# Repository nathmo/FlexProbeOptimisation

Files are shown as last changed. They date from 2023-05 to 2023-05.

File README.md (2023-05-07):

# FlexProbeOptimisation
this repo contain code to compute and properties
of an adjustable stiffness force sensor and optimise
it's parameter to get the best resolution possible

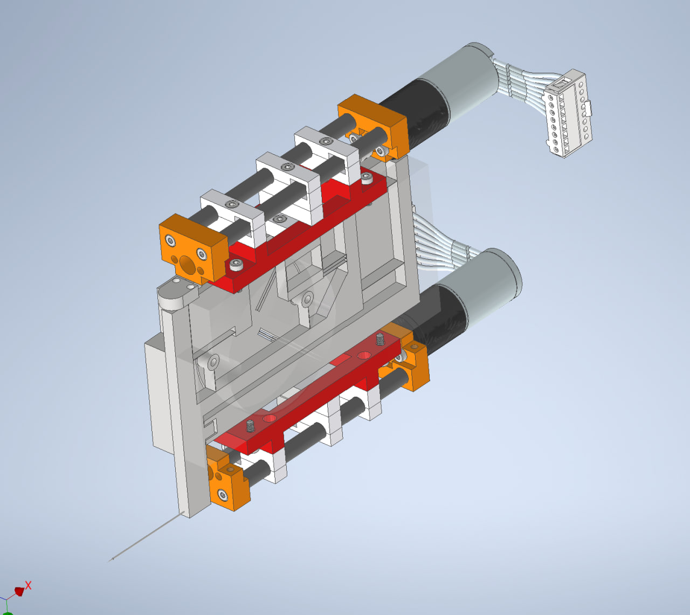
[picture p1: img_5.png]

you will find the parameter in the excel Sheet Settings.xlsx
to import it easily into Autodesk inventor and thus having a parametric desing

after running the code, report.md is updated with the result

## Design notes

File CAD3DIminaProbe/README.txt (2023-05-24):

this folder contain each itteration of our CAD.
Linear axis is the assembly of our LinearAxis alone
RoueMDF is the file for the MDF tunned flex mechanism
V4Roue is the folder with the real CAD of the mechanism

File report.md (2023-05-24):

# Paramètre utiliser pour le calcul des résultat

# 2 Principe de fonctionnement

## 2.6)
Mise en évidence des concepts originaux et explications spécifiques à la solution retenue

# 3) Dimmensionnement

## 3.0 Intro
Target :
Plage de mesure : Fmax > 50 mN

Résolution de mesure : RF < 500 nN. Il s’agit du principal critère d’optimisation du capteur
qui consiste à minimiser la valeur RF(keq,min)

Correction du zéro : le système de réglage doit permettre de corriger des forces parasites
selon l’axe X dans l’intervalle suivant : −1 mN <= Fparasite <= 1 mN

nous allons dabord dimmensionné le système de correction du zéro 
car sa rigidité doit êre prise en compte dans la rigidité total du système.

## 3.1 réglage du zéro
meme actionneur utilisé pour les deux fonction :
q_z = 0.05 mm / tour (vis différentiel : 0.5 mm et 0.45 mm )
d_z = M2.5 et M3
R_alphaz = 1.6° (backlash du reducteur) sinon 0.024245°=360/(512 code/tour * 29 (réducteur))
R_z = 0.003367 micron (q_p/(512*29 (reducteur))) ou 0.22222 micron (backlash)
plage de z max = 0-1mm

résolution point A : Rfz
Plage de réglage demandé : -1mF à 1mF
nombre de position possible du moteur = 4'500
Rfz = deltaFparasite / nombre de position possible du moteur = 2mN/4500= 4.444*10^{-7}[N]

dans le but de diminuer l'impacte de la rigidité de la table sur le reste du systeme,
nous avons utiliser la roue pour diminué la course rensentie par la table
à lame d'un facteur 8. en échange il nous à fallu fournir 8 fois plus de force
donc pas +-1mN mais +-8mN
rigidité des lames : (2 lames*ratio transformation de 8 -> 16 N/m par lame)

nous avons donc essayer de tuner les parametre de notre table pour obtenir la rigidité total de 16 N/m:
avec une table à 2 lamme  mais la longeur devenais trop grande.

Nous avons donc du faire une table avec la plus grande 
hauteur possible : 20 mm de long, 8mm de largeur et 100 um d'épaisseur
nous avons obtenu 220 N/m.

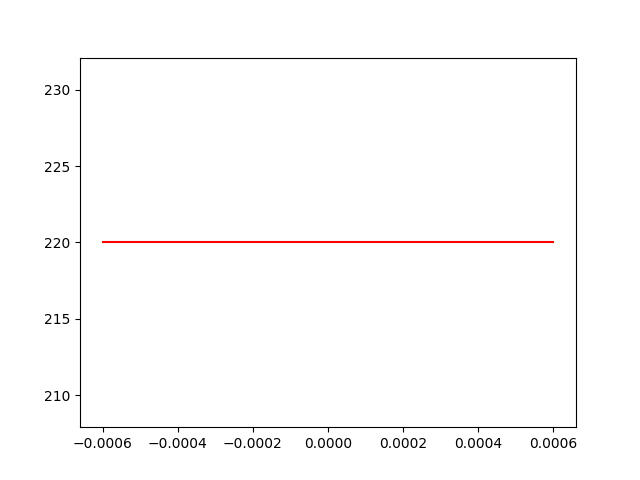
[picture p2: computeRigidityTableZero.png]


soit une plage de réglage de entre -110mN et 110mN
avec une résolution de 0.04888 mN

## 3.2 rigidité 

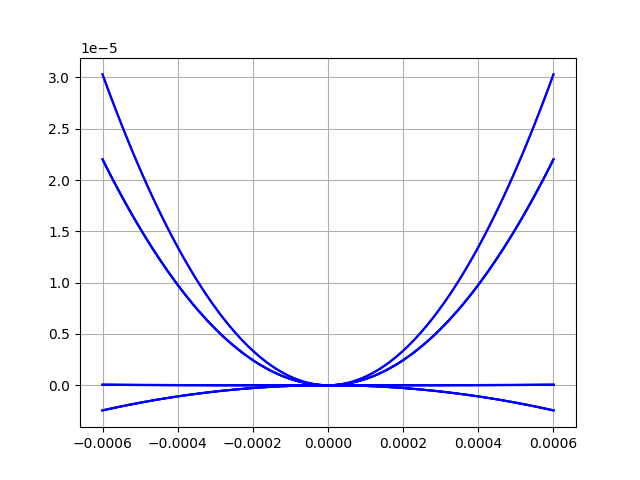
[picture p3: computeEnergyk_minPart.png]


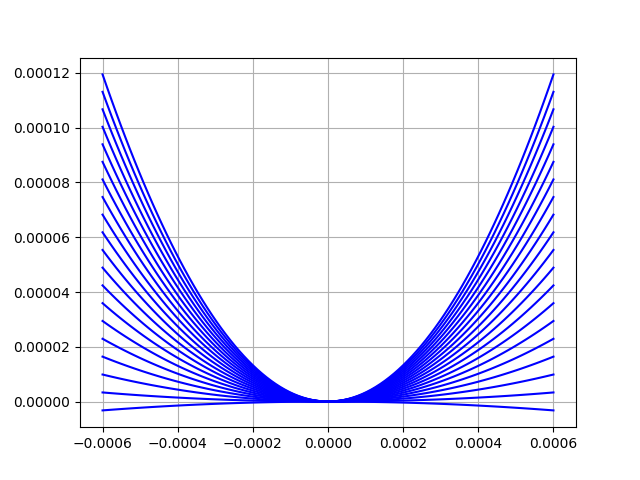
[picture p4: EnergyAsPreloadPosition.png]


meme actionneur utilisé pour les deux fonction :
q_p = 0.05 mm / tour (vis différentiel : 0.5 mm et 0.45 mm )
d_p = M2.5 et M3
R_alphap = 1.6° (backlash du reducteur) sinon 0.024245°=360/(512 code/tour * 29 (réducteur))
R_p = 0.003367 micron (q_p/(512*29 (reducteur))) ou 0.22222 micron (backlash)
plage de p max = 0-1mm

pour déterminer la force que le pusher doit appliquer on graphe le k_eq du system
jusqua trouver les bonnes forces
on aimerais que nos rigidité sois entre : 50 N/m et 

pour la borne minimal on veux une résolution 500 nN
mais la résoltion du cateur est de 10 micron
ce qui nous donne une rigidité à 0.05 N/m ou mieux (0 N/m)

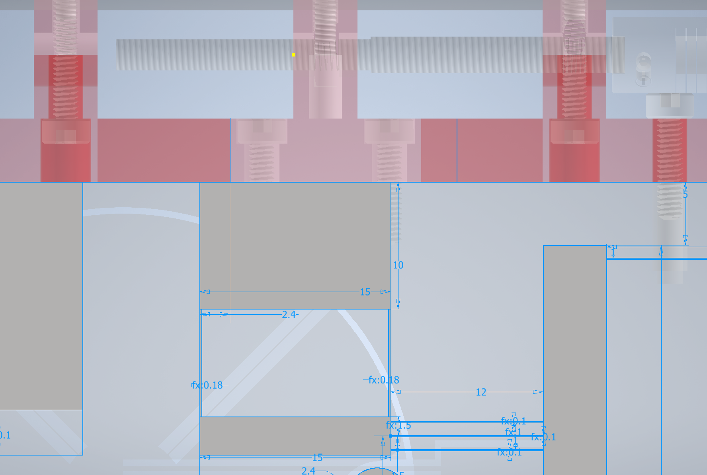
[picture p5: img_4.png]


 (rigidité (N/m) en fonction de la position)
on peut voir que les parametre qui rentre bien dans le range sont :
2.53 N au minimum
2.63 N au maximum
Ces valeurs représente la force à appliquer par lamme.
comme il y as 3 lamme  en parralel, il faut en réalité 
forceMin = 2.53*3=7.59 N
forceMax = 2.63*3=7.89 N
si on voulais maximiser la résoltion il faudrait que le
0.3 N de force revienne à une course d'un 1mm de la table à lamme.
hors cela impliquerais une déformation de 26 mm latérallement.

hors pour des raison géométrique, il est difficile d'avoir une tel course.

nous choississont donc limiter la course de notre table à 2 mm 
de plus nous allons précontraidre la table de 1mm à l'assemblage 
pour profiter de la précharge et supprimer le jeux sur l'actionneur
en plus de profiter d'une meilleure résolution de la force de précharge
dans la région d'interet.

cela impose à notre table d'avoir une rigidité de 7.89N/0.002m=3'945 N/m
et nous pourrons ainsi obtenir une résolution de rigidité.
pour se faire on utilise le nombre de position distincte que l'axe linéaire
peut prendre (4500) répartis sur la plage d'un 1mm ce qui nous donne
3.945 N / 4500 point = 0.8766 mN de résolution pour la force de précharge

de plus on vois qu'on est largement en dessous de la force maximal que 
peut tollérer l'actionneur linéaire.

on voit sur le graphique que la table a lame à bien la rigidité de 3945 N/m
attendu.

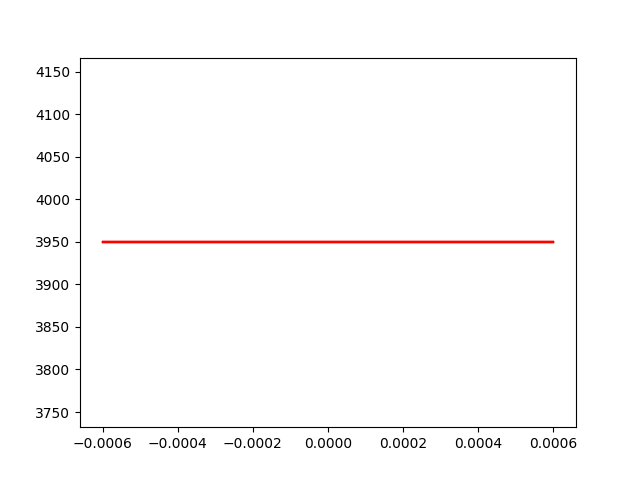
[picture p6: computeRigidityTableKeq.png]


## 3.3 débattement des articulation
(formule mouvement relatif)
0.5 mm sur toute les lames
(légerement plus sur la roue est nécéssaire mais simplifier à 1 mm)

## 3.4 contrainte max flamage + casse chaque lame
(vérifier que les lame supporte une déformation de 2-3mm (demander TRISTAN))

## 3.5 Couple moteur
Nominal torque (max. continuous torque) = 3.33 mNm
réducteur ratio = 29
Nominal Torque on shaft = 29*3.33 mNm = 96.57 mNm
(we neglect loss and add a 20% safety margin at the end)
radius = M3-> 3.2mm/2=1.6mm (on prend le plus gros diametre des 2)
force max = ominal Torque/radius = 60.35 N
donc on se limite à 50 Newton par sécurité
( et  on vois par la suite que la force de précontrainte est inférieur dans tout les cas)

## 3.6 Energie de chaque systeme + total 



Energie total pour le réglage de force sur toute la plage de x
(échelle en unité SI, Joule par metre (avec une précharge N pour chaque courbe))
attention. la force de précontrainte est calculer est calculer par lame.
pour avoir la valeurs total il faut multiplier par le nombre de lame qui transmettent la force
et la au point de rigidité minimum avec un graph pour chaque élément

Energie de chaque systeme + 



## 3.7 dérivé energie = Force en fonction de X

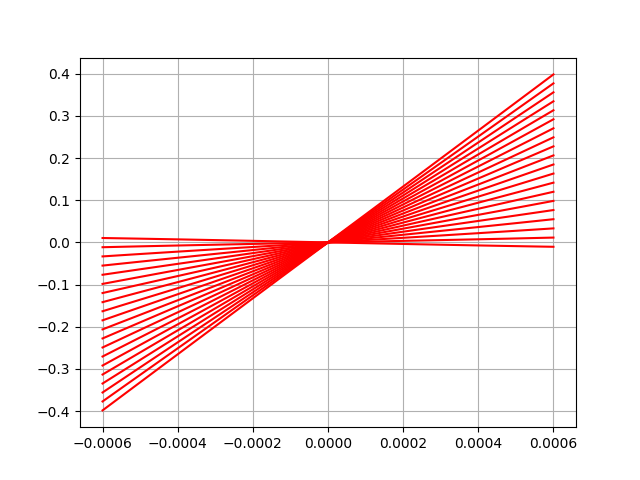
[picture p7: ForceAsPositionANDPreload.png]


(échelle en unité SI, N/m par N)
attention. la force de précontrainte est calculer est calculer par lame.
pour avoir la valeurs total il faut multiplier par le nombre de lame qui transmettent la force
## 3.8  polynome Force en fonction de x degrée 2 (a0 a1 a2)

F (x) ∼= Fpoly3(x) = a0 + a1 · x + a2 · x2 + a3 · x3 ;

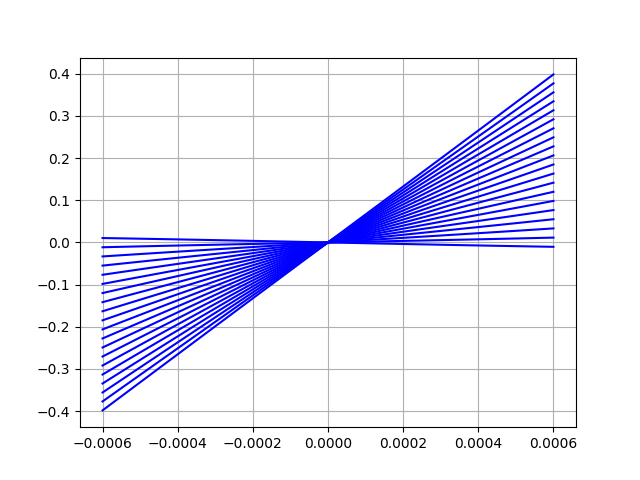
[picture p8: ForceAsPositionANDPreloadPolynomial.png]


## 3.9 k_eq min et k_eq max (dérivé encore)
Determiner la plage de réglage de rigidité de votre mécanisme keq,min 6 keq 6 keq,max correspon-
dants aux réglages pmax , respectivement pmin (note : vérifier bien que keq,min > 0) 

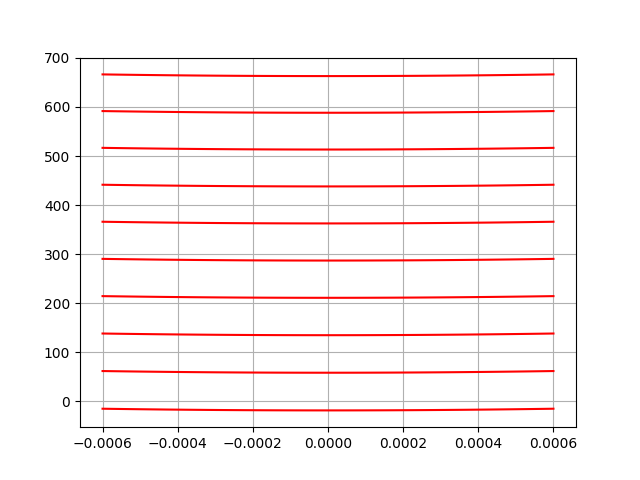
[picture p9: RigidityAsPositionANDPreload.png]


## 3.10 non-linéarité relative mu pour p min et max

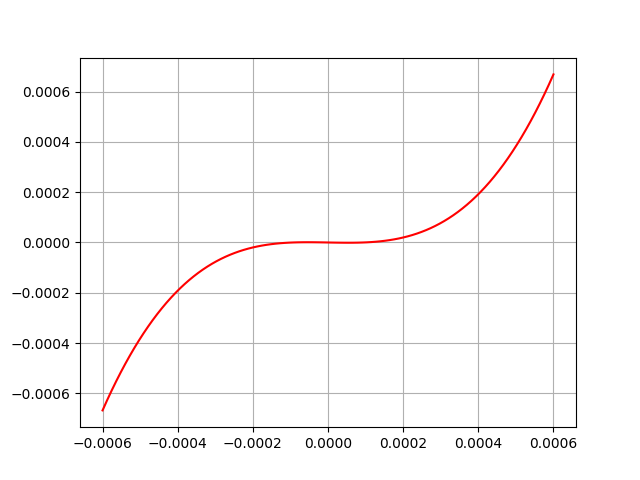
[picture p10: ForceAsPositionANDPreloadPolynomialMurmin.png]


p_min :

mu_r_pmin=-113797755.63251112401

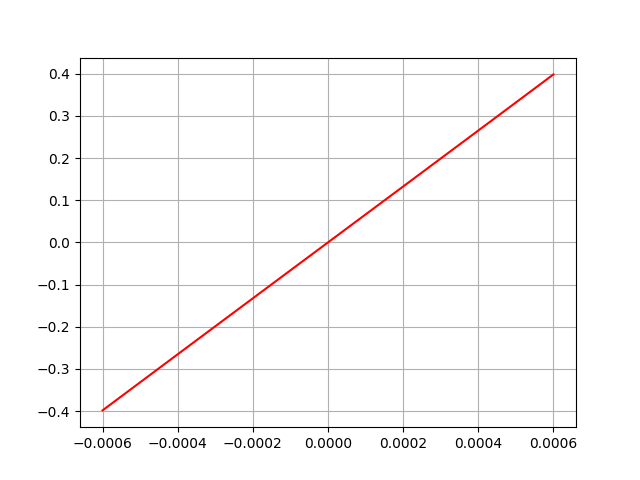
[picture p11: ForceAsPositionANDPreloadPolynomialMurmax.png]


p_max :

mu_r_pmax=4778.5669276376367747

## 3.11 graph de poly + num

Tracer sur un même graphique les fonctions F (x), Fpoly3(x) et Flin(x) 

red = numerical
blue = polynomial
green = linear

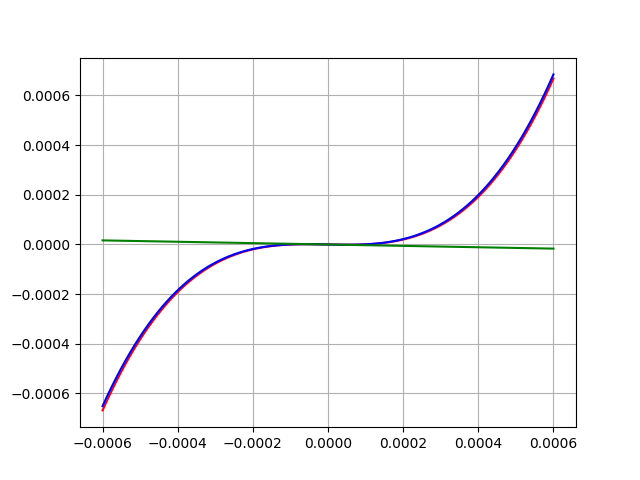
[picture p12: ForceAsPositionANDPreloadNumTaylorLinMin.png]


(nous avons ajouter un leger offset pour voir que les lignes sont bien superposé)

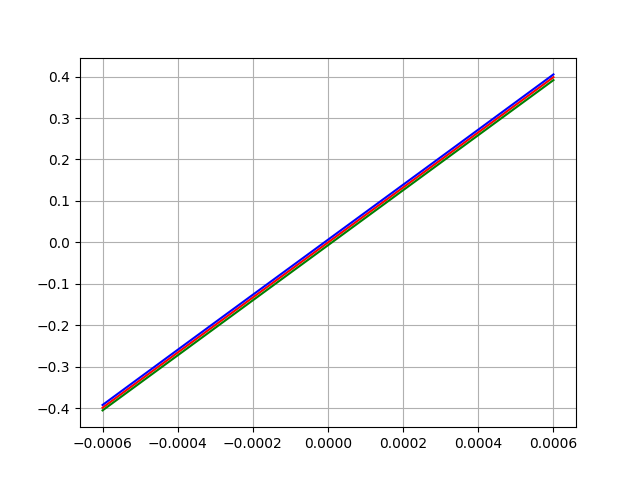
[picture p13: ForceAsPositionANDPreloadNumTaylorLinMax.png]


## 3.12 résolution

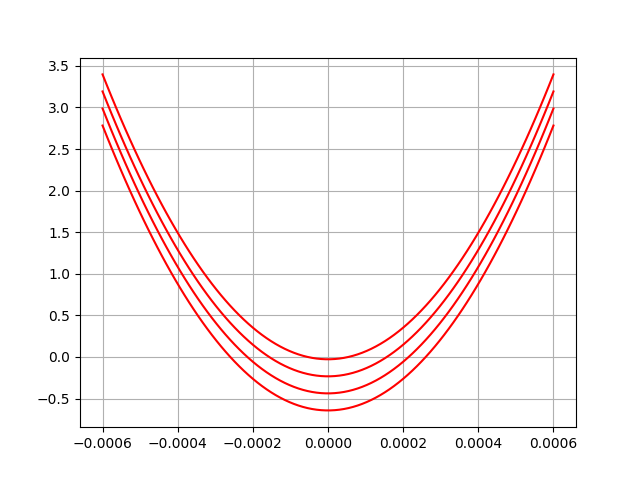
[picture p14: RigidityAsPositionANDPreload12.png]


( chaque ligne montre un réglage de résolution)
ce graphe montre la résolution a 4 point conséqutif de réglable de la précontrainte)
dans le pire des cas on as une rigidité :
RigidityPmin=0.2 N/m

RigidityFPmax=2.5N/m

RFminpmin = 2 nF
RFminpmax = 25 nF

mais dans le meilleures des cas elle peut etre encore meilleure

## 3.13 Force Max mesurable à p_min et p_max
avec Fmax ∼= keq · smax

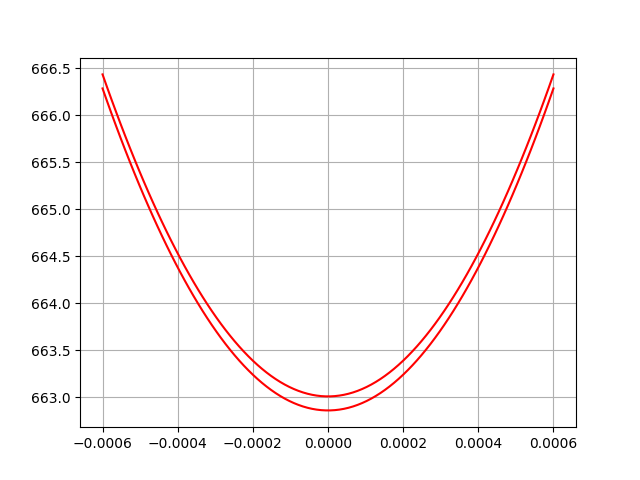
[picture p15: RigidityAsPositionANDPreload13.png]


Fmax_p_min=0.000006810 N (6.8 uN)

Fmax_p_max=0.3405 N

## 3.14 gamme dynamique virtuelle (nombre de point ) de la Force mesurable
(Force MAX / Force min)

DFv : gamme dynamique virtuelle du capteur de force : DFv = Fmax(keq,max)/RF(keq,min)

(échelle en unité SI, N/m par N)
attention. la force de précontrainte est calculer est calculer par lame.
pour avoir la valeurs total il faut multiplier par le nombre de lame qui transmettent la force

DFv=0.3405 N/2 nF=170'250'000

# 5 Construction

## 5.1) choix de construction

## 5.2) Matériaux

aliage titane-6Al-4V

tres peu magnétique
compatible avec le vide, dégaze peu
110 GPa

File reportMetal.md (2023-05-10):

# Paramètre utiliser pour le calcul des résultat

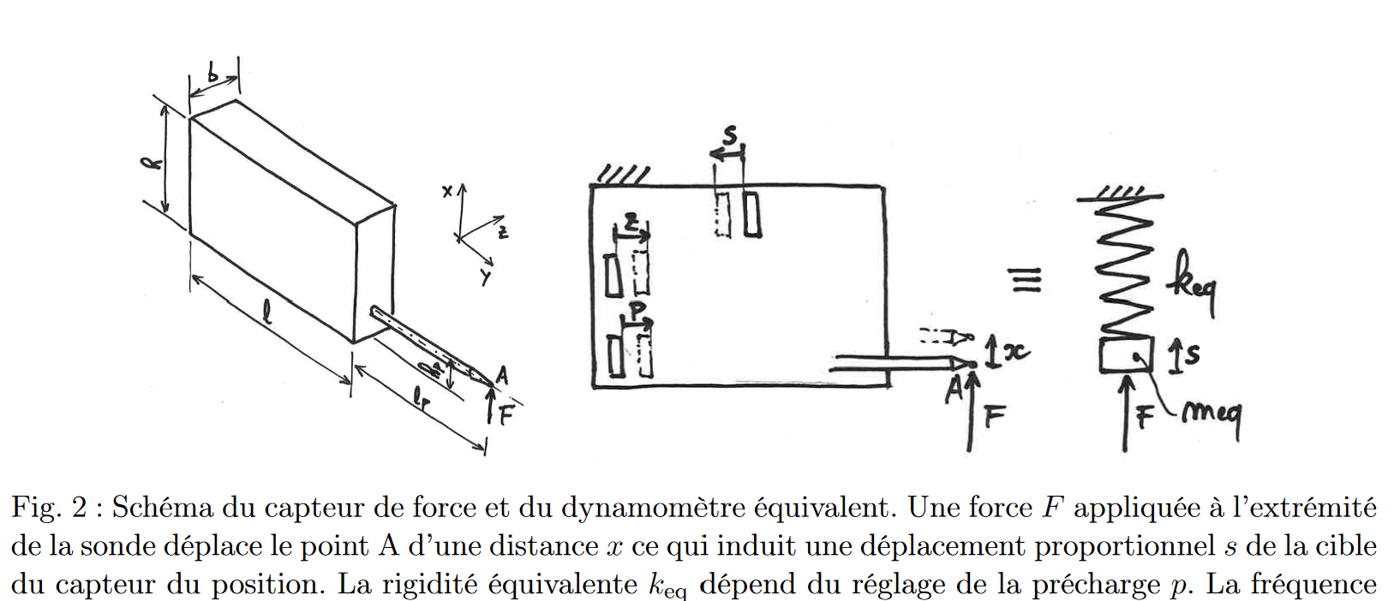
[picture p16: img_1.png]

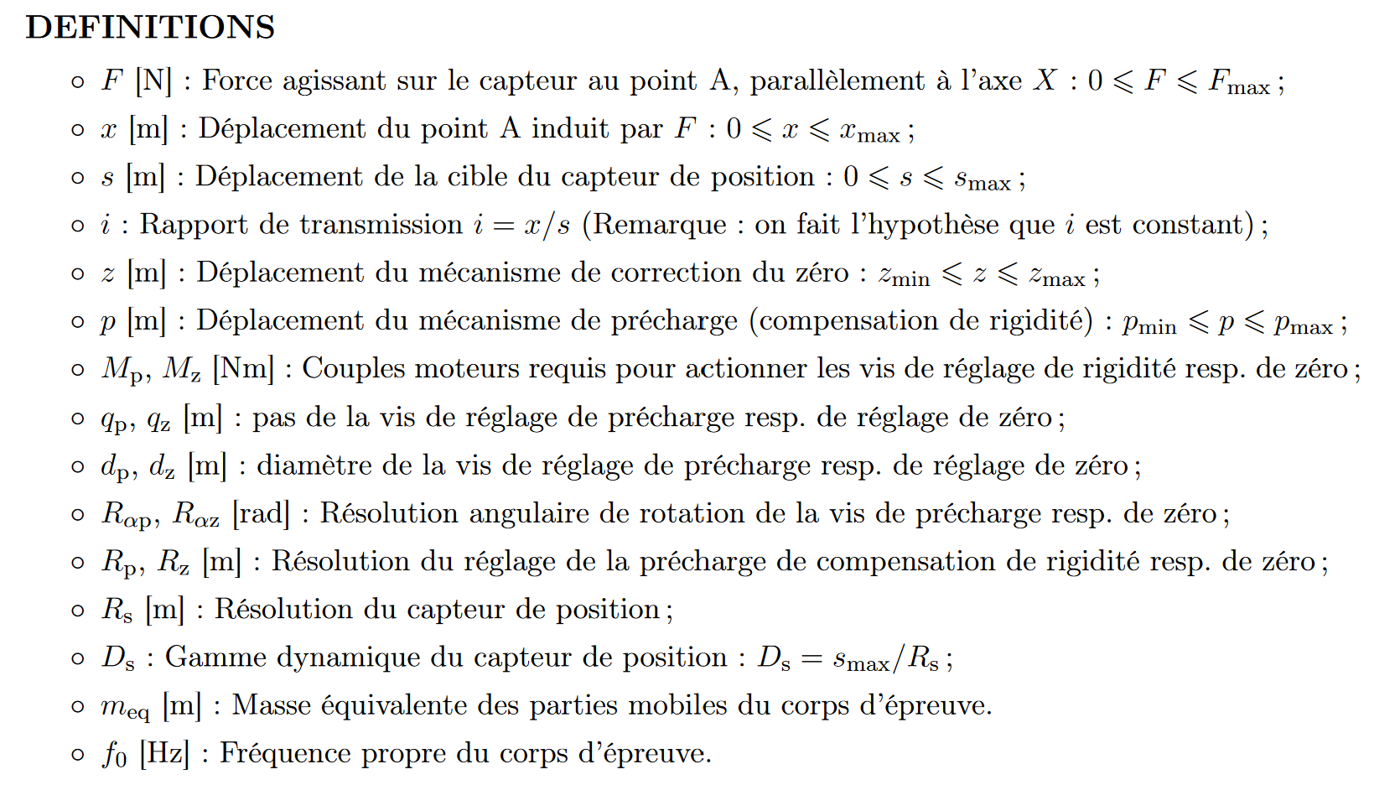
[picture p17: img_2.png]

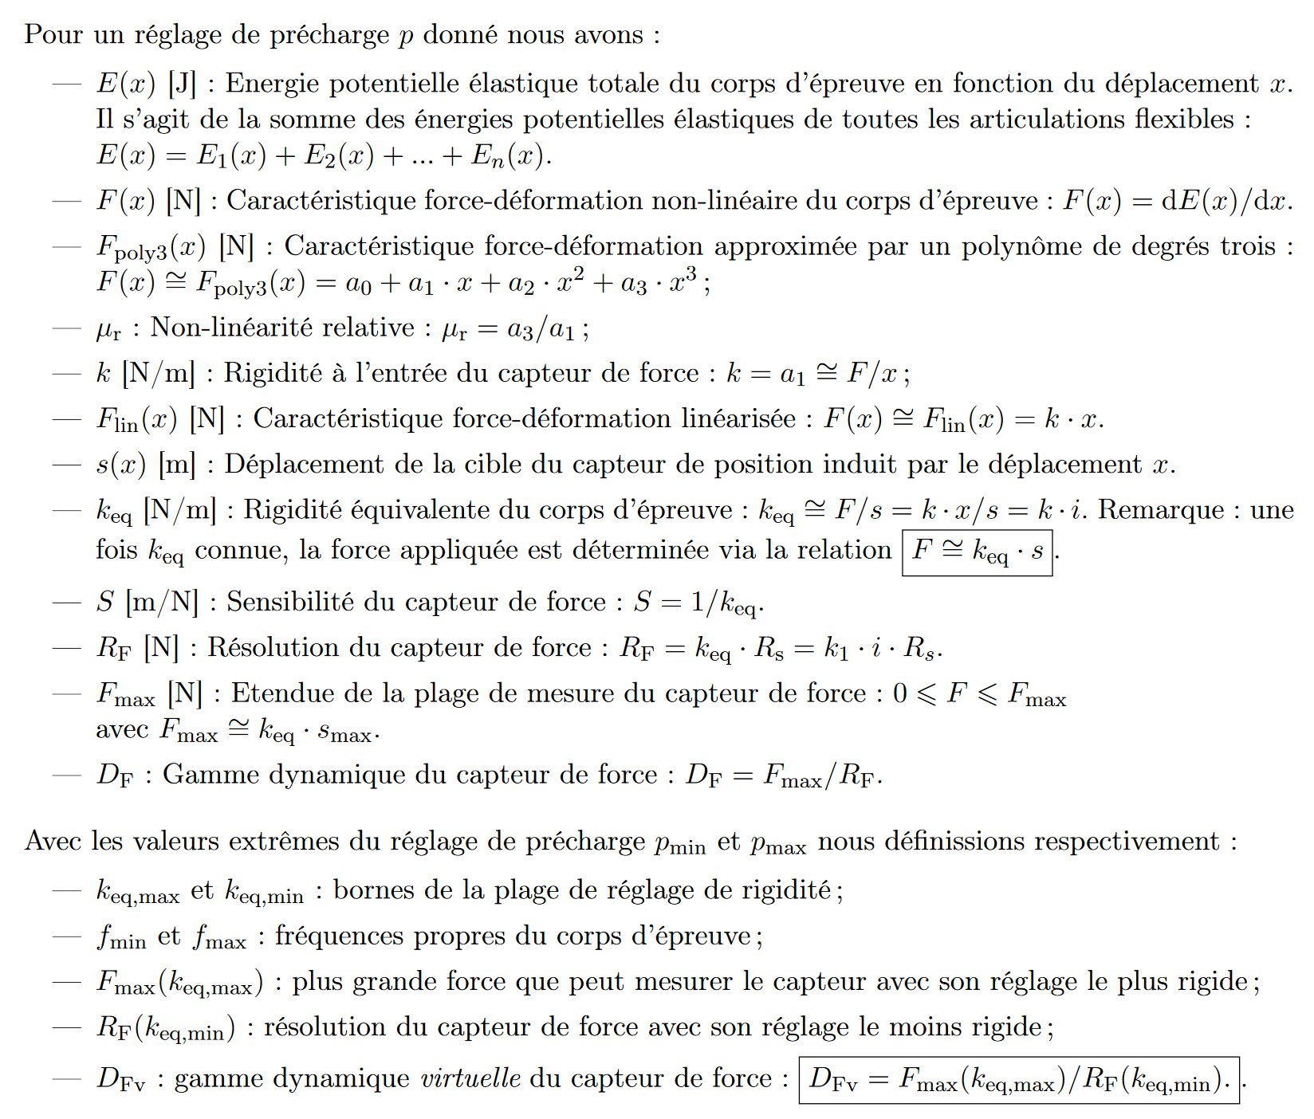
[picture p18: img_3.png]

# 2 Principe de fonctionnement

## 2.6)
Mise en évidence des concepts originaux et explications spécifiques à la solution retenue

# 3) Dimmensionnement

## 3.0 Intro
Target :
Plage de mesure : Fmax > 50 mN

Résolution de mesure : RF < 500 nN. Il s’agit du principal critère d’optimisation du capteur
qui consiste à minimiser la valeur RF(keq,min)

Correction du zéro : le système de réglage doit permettre de corriger des forces parasites
selon l’axe X dans l’intervalle suivant : −1 mN <= Fparasite <= 1 mN

nous allons dabord dimmensionné le système de correction du zéro 
car sa rigidité doit êre prise en compte dans la rigidité total du système.

## 3.1 réglage du zéro
meme actionneur utilisé pour les deux fonction :
q_z = 0.05 mm / tour (vis différentiel : 0.5 mm et 0.45 mm )
d_z = M2.5 et M3
R_alphaz = 1.6° (backlash du reducteur) sinon 0.024245°=360/(512 code/tour * 29 (réducteur))
R_z = 0.003367 micron (q_p/(512*29 (reducteur))) ou 0.22222 micron (backlash)
plage de z max = 0-1mm

résolution point A : Rfz
Plage de réglage demandé : -1mF à 1mF
nombre de position possible du moteur = 4'500
Rfz = deltaFparasite / nombre de position possible du moteur = 2mN/4500= 4.444*10^{-7}[N]

dans le but de diminuer l'impacte de la rigidité de la table sur le reste du systeme,
nous avons utiliser la roue pour diminué la course rensentie par la table
à lame d'un facteur 8. en échange il nous à fallu fournir 8 fois plus de force
donc pas +-1mN mais +-8mN
rigidité des lames : (2 lames*ratio transformation de 8 -> 16 N/m par lame)

nous avons donc essayer de tuner les parametre de notre table pour obtenir la rigidité total de 16 N/m:
avec une table à 2 lamme  mais la longeur devenais trop grande.

Nous avons donc du faire une table avec la plus grande 
hauteur possible : 20 mm de long, 8mm de largeur et 100 um d'épaisseur
nous avons obtenu 220 N/m.


soit une plage de réglage de entre -110mN et 110mN
avec une résolution de 0.04888 mN

## 3.2 rigidité 
meme actionneur utilisé pour les deux fonction :
q_p = 0.05 mm / tour (vis différentiel : 0.5 mm et 0.45 mm )
d_p = M2.5 et M3
R_alphap = 1.6° (backlash du reducteur) sinon 0.024245°=360/(512 code/tour * 29 (réducteur))
R_p = 0.003367 micron (q_p/(512*29 (reducteur))) ou 0.22222 micron (backlash)
plage de p max = 0-1mm

pour déterminer la force que le pusher doit appliquer on graphe le k_eq du system
jusqua trouver les bonnes forces
on aimerais que nos rigidité sois entre : 50 N/m et 

pour la borne minimal on veux une résolution 500 nN
mais la résoltion du cateur est de 10 micron
ce qui nous donne une rigidité à 0.05 N/m ou mieux (0 N/m)

 (rigidité (N/m) en fonction de la position)
on peut voir que les parametre qui rentre bien dans le range sont :
2.53 N au minimum
2.63 N au maximum
Ces valeurs représente la force à appliquer par lamme.
comme il y as 3 lamme  en parralel, il faut en réalité 
forceMin = 2.53*3=7.59 N
forceMax = 2.63*3=7.89 N
si on voulais maximiser la résoltion il faudrait que le
0.3 N de force revienne à une course d'un 1mm de la table à lamme.
hors cela impliquerais une déformation de 26 mm latérallement.

hors pour des raison géométrique, il est difficile d'avoir une tel course.

nous choississont donc limiter la course de notre table à 2 mm 
de plus nous allons précontraidre la table de 1mm à l'assemblage 
pour profiter de la précharge et supprimer le jeux sur l'actionneur
en plus de profiter d'une meilleure résolution de la force de précharge
dans la région d'interet.

cela impose à notre table d'avoir une rigidité de 7.89N/0.002m=3'945 N/m
et nous pourrons ainsi obtenir une résolution de rigidité.
pour se faire on utilise le nombre de position distincte que l'axe linéaire
peut prendre (4500) répartis sur la plage d'un 1mm ce qui nous donne
3.945 N / 4500 point = 0.8766 mN de résolution pour la force de précharge

de plus on vois qu'on est largement en dessous de la force maximal que 
peut tollérer l'actionneur linéaire.

on voit sur le graphique que la table a lame à bien la rigidité de 3945 N/m
attendu.

## 3.3 débattement des articulation
(formule mouvement relatif)
0.5 mm sur toute les lames
(légerement plus sur la roue est nécéssaire mais simplifier à 1 mm)

## 3.4 contrainte max flamage + casse chaque lame
(vérifier que les lame supporte une déformation de 2-3mm (demander TRISTAN))

## 3.5 Couple moteur
Nominal torque (max. continuous torque) = 3.33 mNm
réducteur ratio = 29
Nominal Torque on shaft = 29*3.33 mNm = 96.57 mNm
(we neglect loss and add a 20% safety margin at the end)
radius = M3-> 3.2mm/2=1.6mm (on prend le plus gros diametre des 2)
force max = ominal Torque/radius = 60.35 N
donc on se limite à 50 Newton par sécurité
( et  on vois par la suite que la force de précontrainte est inférieur dans tout les cas)

## 3.6 Energie de chaque systeme + total 

Energie total pour le réglage de force sur toute la plage de x
(échelle en unité SI, Joule par metre (avec une précharge N pour chaque courbe))
attention. la force de précontrainte est calculer est calculer par lame.
pour avoir la valeurs total il faut multiplier par le nombre de lame qui transmettent la force
et la au point de rigidité minimum avec un graph pour chaque élément

Energie de chaque systeme + 


## 3.7 dérivé energie = Force en fonction de X

(échelle en unité SI, N/m par N)
attention. la force de précontrainte est calculer est calculer par lame.
pour avoir la valeurs total il faut multiplier par le nombre de lame qui transmettent la force
## 3.8  polynome Force en fonction de x degrée 2 (a0 a1 a2)

F (x) ∼= Fpoly3(x) = a0 + a1 · x + a2 · x2 + a3 · x3 ;


## 3.9 k_eq min et k_eq max (dérivé encore)
Determiner la plage de réglage de rigidité de votre mécanisme keq,min 6 keq 6 keq,max correspon-
dants aux réglages pmax , respectivement pmin (note : vérifier bien que keq,min > 0) 


## 3.10 non-linéarité relative mu pour p min et max

mu_r=0

## 3.12 résolution


( chaque ligne montre un réglage de résolution)
ce graphe montre la résolution a 4 point conséqutif de réglable de la précontrainte)
dans le pire des cas on as une rigidité :
RigidityPmin=0.2 N/m

RigidityFPmax=2.5N/m

RFminpmin = 2 nF
RFminpmax = 25 nF

mais dans le meilleures des cas elle peut etre encore meilleure

## 3.13 Force Max mesurable à p_min et p_max
avec Fmax ∼= keq · smax


Fmax_p_min=0.000006810 N (6.8 uN)

Fmax_p_max=0.3405 N

## 3.14 gamme dynamique virtuelle (nombre de point ) de la Force mesurable
(Force MAX / Force min)

DFv : gamme dynamique virtuelle du capteur de force : DFv = Fmax(keq,max)/RF(keq,min)

(échelle en unité SI, N/m par N)
attention. la force de précontrainte est calculer est calculer par lame.
pour avoir la valeurs total il faut multiplier par le nombre de lame qui transmettent la force

DFv=0.3405 N/2 nF=170'250'000

# 5 Construction

## 5.1) choix de construction

## 5.2) Matériaux

aliage titane-6Al-4V

tres peu magnétique
compatible avec le vide, dégaze peu
110 GPa

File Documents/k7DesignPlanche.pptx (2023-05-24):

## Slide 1

Groupe 37, Solution 2 : La cassette

Guidages idéaux

Guidages Flexibles

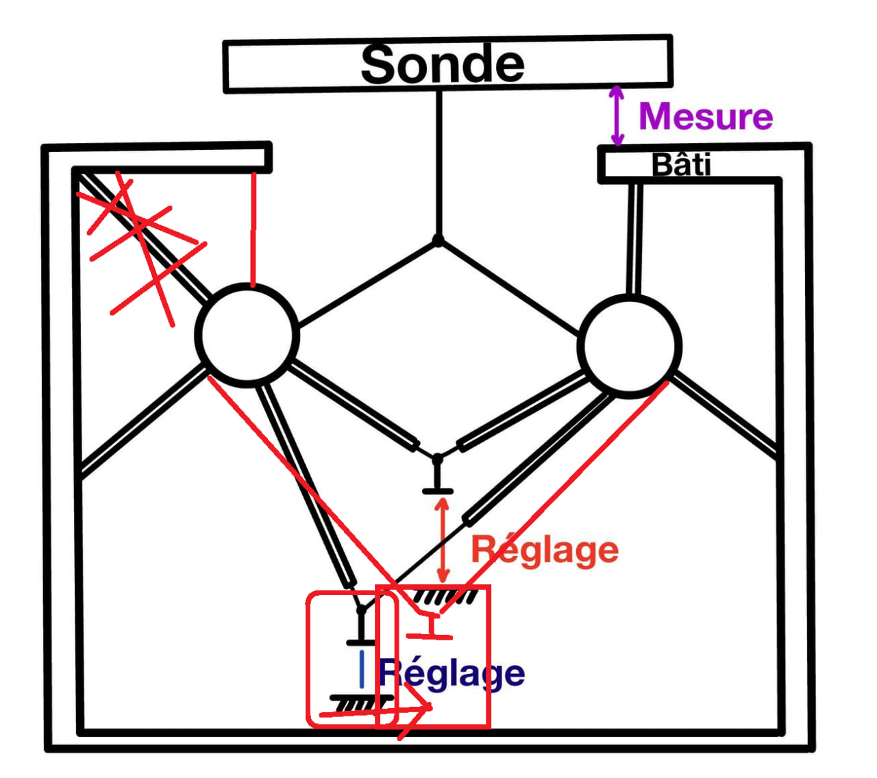
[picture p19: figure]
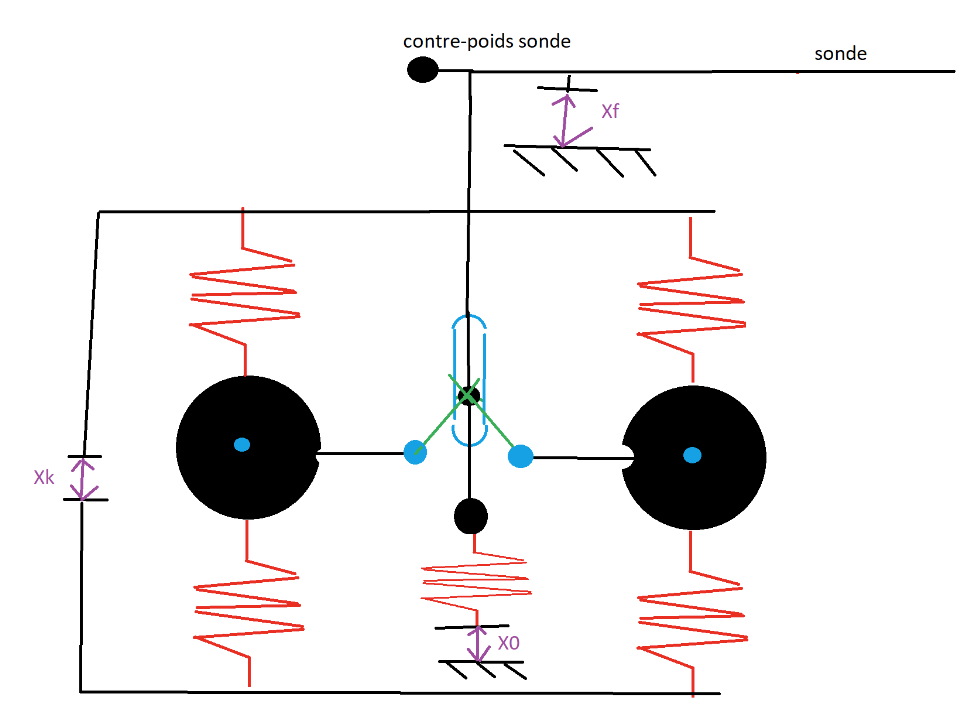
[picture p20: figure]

Mobilité de Grubler

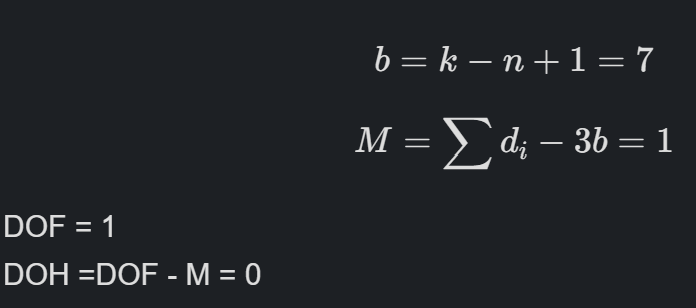
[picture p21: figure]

SFMI

de pars sont implémentions se basant sur un design de référence SFMI,
Il conserve cette propriété.

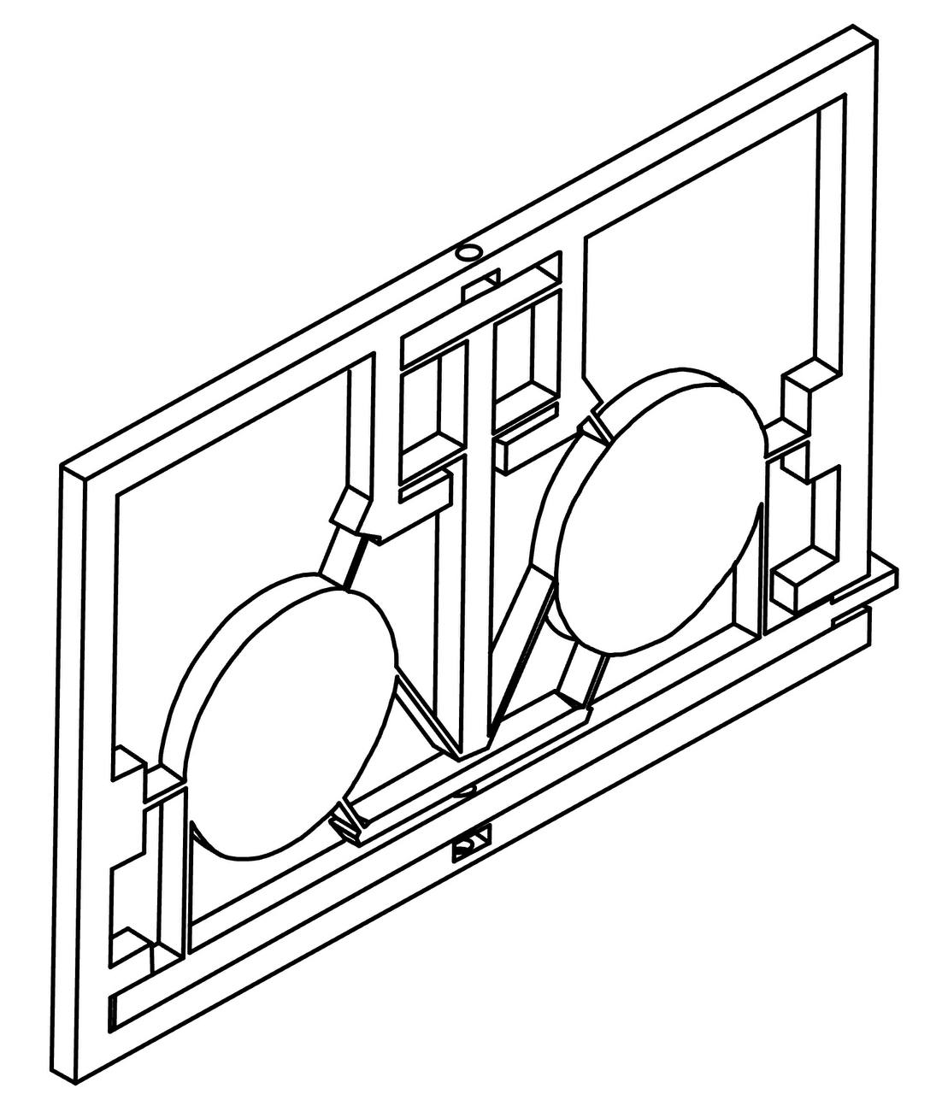
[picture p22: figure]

Ce système de Capteur de force a rigidité et position variable présente l’avantage de pouvoir être réaliser monolitiquement avec une seul pièce (et 2 boulon) mais présente une non-linéarité de la position d'équilibre en fonction de x0 ainsi qu'une non-linéarité de la rigidité en fonction de x0.
Avec un dimensionnement correct, celle-ci peuvent-être vu comme linéaire sur la course de fonctionnement.

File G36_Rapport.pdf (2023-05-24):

Conception de Mécanismes II : Projet Dynabal | Groupe 36
19 MAI 2023 | 1

### Groupe 36

Morand Nathann 296190

Ramirez Felipe 331471

Tankwa Baptiste 346039

Torres Tristan 341042

# PROJET DE CONCEPTION DE MECANIQUES II

# DYNABAL

## Table des matières

2.1.5 | Principe du système vis-écrou (anti-rotation, rattrapage des jeux, guidage vis,
2.6 | Mise en évidence des concepts originaux et explications spécifiques à la solution retenue
| 10
4.1 | Expliquer la séquence de réglage retenue pour obtenir la meilleure gamme dynamique
(rigidité, zéro, fréquence, calibration avec capteur ou tare externes etc.). ET Lister les non-
4.2 | Discuter les effets des tolérances de fabrication (typiquement ±3 µm pour l’usinage par
7.2 | Dessin de détail de la vis | Erreur ! Signet non défini.

## 1 Introduction

Le projet DYNABAL est né de la problématique d’Imina Technologies, souhaitant un capteur de force à rigidité réglable pour ses robots de haute précision, utilisés notamment dans l’industrie des semi-conducteurs.

Dans le cadre du projet DYNABAL, nous avons réalisé un mécanisme que nous avons nommé la Roue. La Roue est un capteur de force équilibré dynamiquement, avec une rigidité variable. Ce rapport détaille son principe de fonctionnement, son dimensionnement, une discussion autour de sa cohérence avec le cahier des charges et des étapes de sa construction.

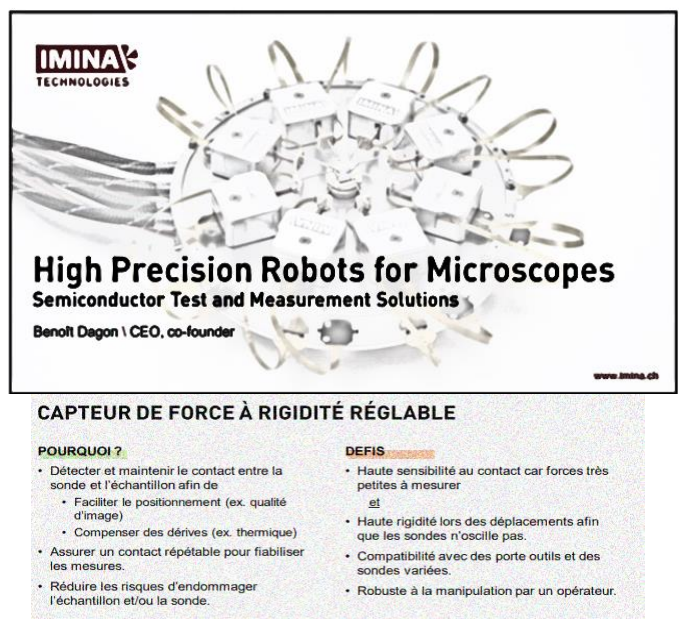
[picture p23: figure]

22 Février 2023

19 mai 2023

6 avril 2023

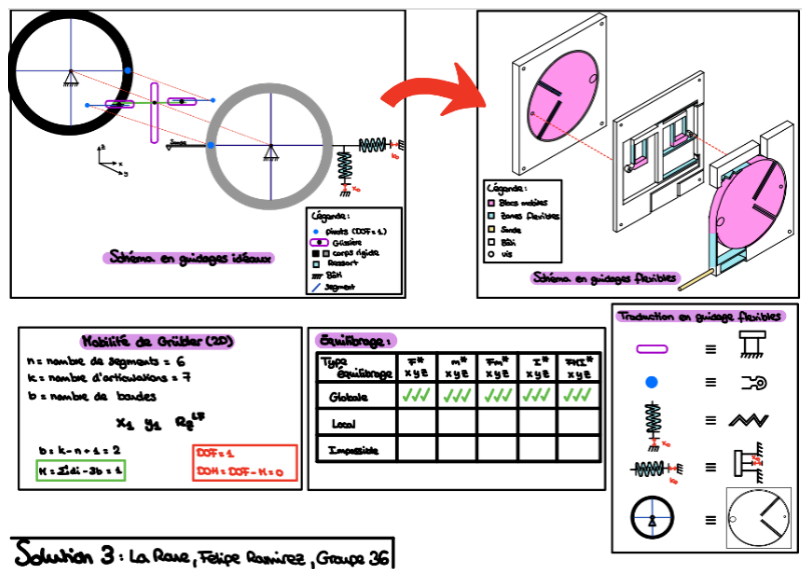
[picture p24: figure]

1.1 : Développement schématique du projet

## 2 Principe de fonctionnement

### 2.1 Explication du principe de fonctionnement

2.1.1 Architecture générale du capteur

Après avoir pris en compte le contenu du cahier des charges, nous avons passé les premières semaines du projet à chercher des idées qui seraient susceptibles de pouvoir respecter l’ensemble des contraintes du cahier des charges. La solution qui est présentée dans la suite du rapport est celle qui nous a semblé à la fois la plus optimale pour le dimensionnement et les performances, mais également pour son élégance. Afin d’optimiser l’espace utilisé, nous avons décomposé le mécanisme en trois couches [voir image qui suit] :

Numéro | Contrainte | Valeurs à atteindre
1 | Utilisation du Capteur de position capacitif Micro-Epsilon CSH05FL | Néant
2 | Sonde de mesure à monter sur le bloc mobile du corps d'épreuve | Néant
3 | Utilisation des moteurs avec Réducteur planétaire pour les réglages | Néant
4 | Ensemble Vis-Écrou pour la conversion des mouvements des moteurs | Néant
5 | Roulements à choisir dans le catalogue SKF | Néant
6 | Accouplements et vis à trouver dans le commerce | Néant
7 | Aucun autre composant commercial | Néant
8 | Le capteur doit s'inscrire dans un parallélépipède | 150x100x50
9 L'axe de la sonde au repos est parallèle à l'axe y les forces à mesurer sont sur l'axe | x | Néant
10 | Dégamement de la sonde | 28mm (h<10mm)
11 | Capteur insensible à l'orientation de la gravité | Néant
12 | Capteur insensible aux accélérations en translation dans toutes les directions | Néant
13 | Capteur insensible aux accélérations en rotation dans toutes les directions | Néant
14 (Equilibrage inertiel : insensibilité du capteur aux vitesses angulaires de son | référentiel) | Néant (Optionnel)
15 | Plage de mesure (Force maximale) | >50mN
16 | Résolution de mesure | <500nN
17 | Correction du zéro | +/- 1mN
18 | Corps d'épreuve réalisé dans un matériau conducteur | Néant
19 | Corps d'épreuve réalisé dans un matériau amagnétique | Néant
20 | (Le système doit supporter des forces parasites sur d'autres directions que x) | +/- 2N (Optionnel)
21 | (Nombre de cycles indicatif) | 1000 cycles/jour 10 ans
22 | (Prix de fabrication indicatif pour petites séries -100 par année-) | 8000.- CHF
23 | (Température de fonctionnement) | 20/30°C

Tableau 2.1: Cahier des charges

Les deux couches extérieures sont deux roues de masse égale fixée au bâti qui servent de contre poids et qui sont reliées par un système d’inversion de rotation, constituant la troisième couche. Le système d’inversion de rotation est nécessaire pour que le mécanisme soit équilibré. En effet, lors d’un mouvement de rotation d’une roue dans un sens, notre système impose le mouvement opposé sur l’autre roue dans le but de rendre le mécanisme insensible aux moments et accélérations extérieurs. La fonction de compensation de rigidité est réalisée par une table à lame préchargée qui se trouve sur la couche centrale. La fonction de réglage de zéro est effectuée par une table à lame qui agit comme un ressort tangent à une des deux roues. Comme indiqué précédemment, ceci permet de compenser les forces parasites induites par la différence de masses entre les diverses sondes avec une force supplémentaire. La sonde est directement liée à la table à lames à rigidité variable pour obtenir une course linéaire verticale et aucun mouvement parasite dans les autres directions.

2.1.2 Principe de compensation de rigidité
Le principe de compensation de rigidité consiste en une table à lames qui va précontraindre la table principale (dite à rigidité variable) comme montré ci-dessous.

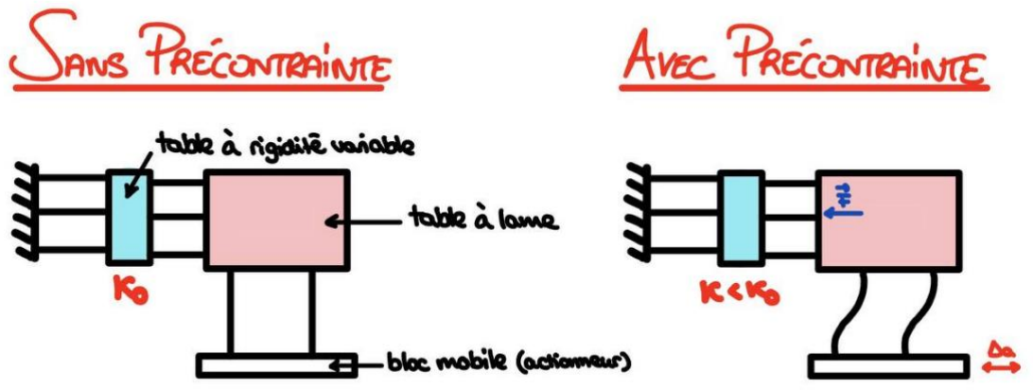
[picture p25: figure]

Ce système a l’avantage de n’induire aucune rigidité parasite supplémentaire.

2.1: Vue éclatée de l'ensemble du système

2.2: Schéma du système de réglage de la rigidité

2.1.3 Principe de l’équilibrage (Analyse qualitative uniquement, sans calculs)

Type d’équilibrage | F* | M* | FM* | I* | FMI*
x | y | z | x | y | z | x | y | z | x | y | z | x | y | z
Local
Global
Impossible

Légende :

F* : Equilibrage en force
M* : Equilibrage en moments FM* : Equilibrage dynamique I* : Invariance inertielle
FMI* : Equilibrage inertielle

Le mécanisme est équilibré en force, car le centre de masse des deux roues de masses égales est fixe. Au sujet des moments, le système d’inversion de rotation permet que le système soit équilibré dynamiquement. En effet, si on applique un moment sur une des roues, l’autre subit un moment opposé.

Remarque : Le tenseur d’inertie restant constant, le mécanisme est donc FMI* grâce aux propriétés des roues.

Nous avons également augmenté considérablement la masse des couches externes, pour que la masse du système d’inversion de rotation soit négligeable et que notre mécanisme reste au mieux équilibré dynamiquement. Nous avons retiré stratégiquement une partie de la masse de la roue afin de compenser la masse de la table à lame et de la sonde afin d’assurer l’équilibrage. Ce point sera développé en annexe.

2.1.4 Principe de réglage du zéro
Le principe du réglage du zéro est mis en place par un ressort placé tangentiellement à une des deux roues.

Tableau 2.2: Description de l'équilibrage du système

2.3: Schéma du système et de son équilibrage


Dans le but de réduire l’impact du système du réglage du zéro sur la rigidité du système, nous avons décalé le point d’application d’une hauteur h par rapport à l’axe de rotation du système. Cela permet une réduction du mouvement de la table lors du mouvement de la sonde. En contrepartie la table doit appliquer une force plus importante, cependant cela ne pose pas de gros problèmes au niveau du dimensionnement.

2.1.5 Principe du système vis-écrou (anti-rotation, rattrapage des jeux, guidage vis, accouplement)

L’actionneur linéaire fonctionne sur la base d’un système vis-écrou. Cependant au lieu d’utiliser une vis à pas fin, nous avons utilisé le principe de vis différentielle. En effet, nous avons utilisé deux vis à pas normaux M2.5 et M3, afin d’avoir une plus grande résolution. Nous les avons configuré comme ci-dessous, pour obtenir un pas virtuel de 50 µm (7 x meilleur qu’avec des vis à pas fins (350 µm au mieux)) :

2.4: Schéma du principe de réglage du zéro

2.5: Schéma de l'actionneur

Cet actionneur offre une précision 0.22 µm et une course de 1 mm. Un des désavantages de ce type de système est son encombrement. En effet, notre actionneur est assez long et il occupe un volume de 20*20*130 mm. Outre la précision supérieure, l’avantage d’un tel système réside dans l’absence de roulements à billes. Les efforts sont entièrement concentrés sur les deux écrous. Le seul effort que doit éventuellement reprendre le moteur est son propre poids ainsi que son support qui rentre largement dans les contraintes admissibles de celui-ci.

Afin d’assurer le couplage entre l’axe et le moteur, nous avons utilisé un cardan flexible pour pallier les éventuelles erreurs d’ajustements.

Finalement, pour le rattrapage des jeux, nous avons précontraint la table à lame de réglage de la rigidité. Cela permet d’assurer que la force subie par les écrous soit toujours dans la même direction, réglant ainsi le problème du jeu tout en augmentant la résolution du système dans la plage utile de réglage.
En ce qui concerne le réglage du zéro, nous avons préféré ajouter un ressort de précontrainte entre les 2 écrous, le réglage du zéro prenant à la fois des valeurs positives et négatives pour la position relative, il était plus complexe de précontraindre la table à lame.

Pas virtuel de 50 µm

2.6: Schéma du principe de vis différentielle

### 2.2 Schéma cinématique du corps d’épreuve représenté avec des articulations idéales

### 2.3 Calcul de la mobilité du corps d’épreuve (Grübler) et discussion des hyper statismes

Pour le calcul des mobilités de Grübler en 2D, notre mécanisme possède 6 segments, 7 articulations. Par calcul, nous trouvons qu’il possède deux boucles. Pour nos degrés de liberté :
x1 | y1 | RzLF

Il peut seulement effectuer une rotation en z dans le plan, les translations selon x et y sont bloquées par le pivot relié au bâti. Le degré de mobilité étant de 1 et égal au degré de liberté. Notre mécanisme ne possède pas d’hyperstatismes.

### 2.4 Implémentation de la cinématique du corps d’épreuve en guidages flexibles

Étant donné que nous utilisons notre système sur de très petites courses, nous avons traduit les glissières par des tables à lames. Les mouvements parasites sont négligeables dans ce cas.

2.7: Schéma cinématique du mécanisme

2.8: Schéma de la traduction des glissières

2.9: Schéma de la traduction des roues

Les deux roues ont été traduites par des pivots munis de deux lames (Pivots RCC). Cette traduction nous convient car elle possède un seul degré de liberté local (Rz). Les deux lames contraignent la roue à seulement tourner sur des très petites courses.

La fonction de réglage du zéro est réalisée par une table à lames, qui agit comme un ressort ajoutant une force sur la sonde.

La fonction de compensation de rigidité est représentée par une table à lames, qui peut être comprimée.

2.5 Discussion qualitative de la linéarité du rapport de transmission (i ≈ constante).
Le rapport de transmission du mécanisme est constant, nous n’amplifions pas le mouvement.
En conséquence notre rapport de transmission est constant i = 1.

### 2.6 Mise en évidence des concepts originaux et explications spécifiques à la solution retenue

Nous avons retenu cette solution, car par son implémentation et son originalité font d’elle la solution la plus élégante des trois que nous avons proposées lors du rendu intermédiaire.

Premièrement, notre mécanisme est SFMI*. Il est équilibré en inertie. (Voir le 2.1.3) Les deux roues implémentées en pivot RCC sont équilibrés dynamiquement grâce au système d’inversion de rotation, mais aussi d’un point de vue inertiel.

Deuxièmement, nous utilisons le principe de vis différentielle pour notre actionneur. En utilisant deux vis à pas normal en configuration différentielle, nous obtenons une résolution 7x meilleur qu’avec des vis à pas fin. (Voir le 2.1.5).

Troisièmement, nous avons précontraint le système de compensation de rigidité pour obtenir une meilleure résolution sur la plage utile et donc améliorer la résolution maximale.

Quatrièmement, nous avons fait un système multicouche pour pouvoir maximiser la masse des roues, ainsi être moins sensible aux variations de masses due aux tolérances. Un système multicouche permet également d’avoir le système d'inversion de rotation et de compensation de rigidité sur une couche aussi fine que possible pour en limiter la rigidité afin de maximiser la résolution.

2.10: Schéma de la traduction de la fonction du réglage du zéro

2.11: Schéma de la traduction de la fonction de compensation de rigidité

Cinquièmement, nous avons rajouté un système de protection du mécanisme, qui permet lorsqu’une trop grande force est appliquée d’empêcher la transmission de cette force aux autres parties du mécanisme.

2.12: Schéma du système de protection du mécanisme

## 3 Dimensionnement du mécanisme

### Introduction

D’après le cahier des charges, nos objectifs lors de cette partie traitant du dimensionnement du mécanisme du projet DYNABAL sont les suivants :

- FMAX ≥ 50 mN, la grandeur FMAX nous permet de définir la plage de mesure du capteur.
- RF ≤ 500 mN, la grandeur RF correspond à notre résolution de mesure, il s’agit du principal facteur d’optimisation.
- Pour la correction du zéro, le système doit permettre de compenser des forces dans l’intervalle −1 mN ≤ Fparasite ≤ 1 mN, ce système permet donc de faire la tare. Il a été expliqué dans le paragraphe 2.1.4.

Cette partie explicite donc les diverses étapes et calculs démontrant que notre système convient aux besoins énoncés précédemment.

### 3.1 Réglage de la rigidité

Le système vis-écrou, explicité en 2.1.5, permet d’obtenir les caractéristiques suivantes :

- qp = 0.05 mm/tour (écart entre les pas)
- dp = M2.5 / M3
- Rαp =
- Rp = qp Rαp

1
360

≃ 3.3611 nm (ou 0.22µm avec le backlash)

Avant de pouvoir calculer la résolution des divers réglages, il faut tout d’abord définir les facteurs limitants. Ils sont les suivants : la résolution du capteur de position et le backlash du réducteur.

On trouve que le facteur limitant est le backlash du réducteur, puis nous calculons notre résolution angulaire Rαz et la résolution de réglage de la rigidité Rp, cependant celle-ci n’a pas besoin d’être prise en compte après discussion avec le Prof. Henein. Notre facteur limitant est donc notre vis. (les deux calculs sont présentés)

nécessaire.

Nous avons suivi le cheminement décrit dans la page qui suit pour en arriver à trouver la rigidité

3.1 Schéma du principe de vis différentielle

### 3.2 Réglage du zéro

Nous utilisons le même actionneur pour le réglage du zéro et le réglage de la rigidité. On obtient donc les mêmes valeurs que précédemment.

- qz = 0.05 mm/tour (écart entre les pas)
- dz = M2.5 / M3
- Rαz =
- Rz = qz Rαz

1
360

≃3.3611 nm (ou 0.22µm avec le backlash)

Nous avons effectué une simulation des paramètres de la table pour obtenir une rigidité totale de 16 N/m (2 N/m pour avoir les +- 1mN demandé par le cahier des charges qu'il faut multiplier par 8 à cause de l'arrangement de la table à lames). Cependant la longueur nécessaire n’aurait pas respecté le cahier des charges. Nous avons donc réalisé une table avec la plus grande hauteur possible : 20 mm de long, 8mm de largeur et 100 μm d'épaisseur. Nous avons obtenu une rigidité de 220 N/m. Soit une plage de réglage située entre -13.75mN et 13.75 mN avec une résolution de 184.8 nN. (RFz = 184.8 nN)

### 3.3 Débattement des articulations

Pour le calcul des débattements des articulations, nous avons commencé par établir les articulations susceptibles de poser des problèmes, en analysant notre système nous remarquons que le pivot RCC est le point critique du système au niveau des débattements. Nous allons donc nous assurer que ceux-ci ne posent aucun problème.

Premièrement, il est nécessaire de vérifier la plage de mouvement du pivot RCC, en faisant un calcul simple nous obtenons la différence de distance entre les deux points d’ancrage :

∆x =

rroue

rp_app

∗ xmax =

23mm
20mm

∗ 0.5mm = 0,575mm

L’espace que le système a pour tourner étant de 0,95mm celui-ci est donc largement suffisant pour éviter une quelconque collision sur la plage de mesure du système.

Nous devons également vérifier que les mouvements parasites des pivots RCC n’induisent pas de collision, nous utilisons la formule :

|PP

′
| =

(9δ

2 + 9δ + 1)θ

2
l
15cos (

x
r

)

= 3.2μm δ =

p
l

(Voir figure 3.2)

L’espace libre étant de 500μm celui-ci est également largement suffisant.

Les débattements des articulations critiques ne causent donc aucun problème dans notre mécanisme.

### 3.4 Contraintes maximales dans le domaine autorisé

Pour l’ensemble de ces calculs, nous nous sommes basés sur les courses maximales admissibles (qui sont directement dépendantes des contraintes maximales admissibles par le système), pour les formules, nous nous sommes basés sur celles qui sont trouvables dans Conception des structures articulées à guidages flexibles de haute précision, la thèse du Prof.Henein.

Nous avons donc choisi comme matériel l’alliage Ti-6Al-4V (caractéristiques en fin de rapport), qui a donc une contrainte maximale admissible de σyield = 880MPa. Nous avons également choisi un facteur de s´sécurité S = 1.5 pour tous nos calculs afin d’être certains que notre mécanisme résistera aux contraintes auxquelles il sera soumis ainsi qu’à des contraintes supplémentaires inconnues.

Nous avons donc σadm ≃ 586.5MPa, c’est cette valeur que nous avons utilisée dans les calculs qui suivent.

3.4.1.1 Réglage du zéro
Pour le réglage du zéro, nous utilisons une table à lame classique, d’après le document mentionné précédemment. Ici h = 0.1 mm, l = 20 mm.
fadm = | = 7.1*10⁻³
[m]
| freal = 1*10⁻³ [m]

Nous pouvons vérifier que la course du réglage du zéro est supérieure à la course admissible par celui-ci (et donc que la contrainte qu’il subit lors de sa plage de mouvement est inférieure à la contrainte maximale autorisée) avec le facteur de sécurité défini précédemment.

3.4.1.2 Réglage de la rigidité
Il s’agit également d’une table à lame nous réutilisons donc la formule précédente avec les valeurs suivantes : h = 0.2mm, l = 12.125mm.
fadm = | = 1.3*10⁻³
[m]

freal = 1*10⁻³
[m]

La course est dans les limites tolérables avec le facteur de sécurité, néanmoins la marge entre la course admise et la course réelle est faible, nous pouvons donc nous poser des questions sur la résistance à la fatigue de ce mécanisme.

3.4.1.3 Tables à 3 lames comprimées
Les deux tables sont similaires mais avec des dimensions différentes, nous avons choisi le pire des cas, d’après Conception des structures articulées à guidages flexibles de haute précision, de Simon Henein, nous avons :

Pour la force où le lames ont la plus faible course admissible, on obtient donc :

Nous pouvons donc voir que la course est inférieure à la course maximale admise dans le cas où l’on ne compense pas la rigidité. Cependant, dans le cas où nous commençons à compenser la rigidité, nous pouvons considérer la formule valable à la limite du flambage donc avec N = NC.

Même à la limite du flambage, le système résiste à la course nécessaire, ce calcul permet également de vérifier que nous ne dépassons pas la limite du flambage qui correspond à NC = 30.16N.

3.4.1.4 Pivots RCC
La course maximale angulaire admissible pour un pivot RCC est donnée par la formule :

La course angulaire maximale du pivot est donnée par

Les pivots RCC n’ont donc pas de problèmes au niveau des courses admissibles.

3.4.1.5 Pivots à Lames
La course maximale pour une lame, subissant une force perpendiculaire est de :

### 3.5 Couples moteurs

D’après le document sur les vis que nous pouvons trouver dans le cours, nous avons la formule suivante :

Avec :

Nous voulons calculer si le moteur a la capacité de nous faire atteindre notre course maximale sur la table avec la rigidité la plus importante. (Ici la table de réglage de la rigidité K = 3945 N/m), nous
posons ainsi | et nous obtenons :

Le couple maximal qu’il est possible de fournir est donné par la datasheet du moteur et est de 3.33mN.m, cependant en utilisant le réducteur, celui-ci est multiplié par 29 et d’où

En effet, en divisant le moment maximal par le moment critique, nous obtenons | , ce qui
est largement suffisant.

### 3.6 Energie de chaque système et totale

Remarque : Dans l’ensemble de cette partie h correspond à l’épaisseur d’une lame et b sa largeur, et

Nous avons tout d’abord listé les divers systèmes pouvant stocker de l’énergie ainsi que leur rigidité :

l’équivalence; ,, ce qui nous donne

Pivots RCC (2x) : | . . Pour la conversion, nous avons

Table à lames principale (sans précontrainte) : il s’agit d’un système qui peut être interprété comme deux tables à 3 lames qui peuvent être comprimées :

Lames Pivots (2x) : S’agissant d’une lame nous avons

Celle-ci étant attachée à une de nos roues, nous pouvons dériver son mouvement en fonction
x par de la simple trigonométrie, nous obtenons donc | , il s’agit donc de la partie
linéaire de notre système. Il n’est pas possible de calculer une rigidité équivalente sans faire une approximation.
Table à lames de réglage du zéro, nous obtenons la rigidité suivante :
Avec le système de réduction, nous avons | le rayon de notre bras de
levier, ainsi | et nous obtenons :

Enfin, nous avons calculé les énergies respectives suivantes :

Pivots RCC :

3.2 : Schéma du pivot RCC


Table à lames principale :

Lames Pivots :

Table de réglage du zéro :

Ainsi, pour calculer l’énergie totale il suffit de sommer ces différentes énergies :

Energie totale pour le réglage de force sur toute la plage de x : échelle en unité SI, Joule par mètre (avec une précharge comprise entre 3.945 N et 7.89 N pour chaque courbe, force tirée de la section 3.1)

Energie de chaque système pour le réglage de force sur toute la plage de x : échelle en unité SI, Joule par mètre (avec une précharge comprise entre 3.945 N et 7.89 N pour chaque courbe)

### 3.7 Force en fonction de x

On dérive partiellement l’énergie par rapport à x (qui représente le déplacement de la sonde en [m]) pour trouver la force.

Force en fonction de x : échelle en unités SI, N/m

### 3.8 Polynôme approximant F(x)

Nous avons approximé F(x) par un polynôme dont voici le graphe. On peut voir que le graphe est extrêmement proche de celui de la section 3.7 ce qui montre que le polynôme approxime bien nos courbes.

Force en fonction de x : échelle en unités SI, N/m

### 3.9 Plage de réglage de rigidité


Le graphe montre la rigidité [N/m] en fonction de la position de la sonde [m] pour différents réglages de précontrainte. On peut voir que celle-ci est presque linéaire et varie peu avec le déplacement de la sonde (sauf lorsqu’elle est très proche de la rigidité nulle où la non-linéarité devient non négligeable)

Pour pmin (7.89 N), on obtient une rigidité minimum de 0.07562 N/m, et pour pmax (3.945 N), on obtient une rigidité maximum de 675 N/m.

### 3.10 Non-linéarité relative

Après avoir obtenu les coefficients du polynôme en utilisant l’interpolation nous trouvons que la non-linéarité relative pour pmin est : µr_pmin=7 931 363.36

Graphe montrant la force [N] en fonction du déplacement [m] lorsque la rigidité est presque nulle (0.075N/m)

Nous trouvons également que la non linéarité relative pour pmax est : µr_pmax = 4 757.85

Graphe montrant la force [N] en fonction du déplacement [m] lorsque la rigidité est maximale, dans ce cas, la courbe est presque linéaire

### 3.11 Graphe des fonctions F (x), Fpoly3(x) et Flin(x)

Nous avons représenté le cas linéaire en vert, F(x) en rouge et son approximation polynomiale est en bleu. Le premier graphique montre la force en fonction de la position quand la rigidité est presque nulle :


Graphe montrant les fonctions F(x), son approximation polynomiale et son approximation linéaire

Le second graphe lui montre la même chose quand la rigidité est maximale

L’échelle du graphe précédent est différente des autres pour faciliter la visualisation de la non-linéarité.

Graphe montrant les fonctions F(x), son approximation polynomiale et son approximation linéaire

### 3.12 Résolution

Graphe montrant la force en fonction de la position pour différents réglages de résolution proche de zéro.


Chaque courbe montre la force en fonction de la position pour différents réglages de résolution proche du zéro. On obtient les valeurs suivantes :

RigidityxminPmin= 0.00605 N/m

RigidityxmaxPmin= 0.0756 N/m

RFxminPmin = 0.0605 nN

RFxmaxPmin = 0.75626 nN

On peut constater que la résolution n’est pas linéaire quand la sensibilité est maximale mais cela peut être un avantage en termes de plage dynamique à la condition de devoir interpréter les valeurs via une lookup table.

### 3.13 Force maximale mesurable à p_min et p_max

Graphe montrant la force maximale mesurable à pmin et pmax

Le graphe fait un large zoom sur l’axe Y, comparativement, la non-linéarité est négligeable dans ici

La force maximale est environ égale à la rigidité équivalente multipliée par le déplacement maximal de la cible du capteur de position. FPmaxXmax =0.3405 N pour pmax

La force minimale mesurable avec la sensibilité au minimum : FPmaxXmin =6.8 uN avec pmax

### 3.14 Gamme dynamique

Remarque : La force de précontrainte est calculée par lame. Pour avoir la valeur totale, il faut multiplier par le nombre de lames qui transmettent la force.

DFv =

0.3405 N
0.0605 nN

= 5'628'099'173.

### 3.15 Résultats


2.3: Résumé des objectifs atteints par notre capteur

## 4 Discussion

### 4.1 Expliquer la séquence de réglage retenue pour obtenir la meilleure gamme dynamique (rigidité, zéro, fréquence, calibration avec capteur ou tare externes etc.). ET Lister les non-conformités avec le cahier des charges et discuter leur

impact.

Dans le but de maximiser la résolution, la gamme dynamique et la force maximale mesurable, nous avons fait les choix suivants :

Premièrement, nous avons essayé de minimiser au maximum le nombre de lames pour qu’il y ait aussi peu de rigidité à compenser que possible. Cela permet d’obtenir une meilleure résolution. En ce qui concerne la table à 3 lames tenant la sonde. Il nous a été nécessaire d’utiliser des tables à trois lames afin d’annuler l’effet de potentiels moments sur le système.

Deuxièmement, on fait en sorte de minimiser la rigidité équivalente du système du réglage du zéro, car il ajoutait une rigidité fixe de 2 N/m. Cette rigidité fixe est due à la contrainte du cahier des charges. Pour diminuer la course effective de la sonde par rapport au ressort de réglage du zéro, nous avons utilisé la roue comme un bras de levier. Pour des raisons géométriques, nous n’avons pas pu avoir la rigidité aussi faible que possible, car cela impliquait des lames trop grandes. Troisièmement, les lames ont été optimisées, pour qu’elle soit aussi fines et longues que possible. Quatrièmement, on a fait en sorte que la rigidité pour la table à lames de précontrainte de compensation de rigidité permette, avec la course du moteur, qu’elle rentre au mieux dans la plage de valeurs imposées par le cahier des charges.

Remarque : Nous avons utilisé un script python qui, lorsqu’on lui donne les différents paramètres géométriques dans un Excel lié au CAD (design 3D paramétrique), génère tous les graphes et calculs propre à la partie dimensionnement pour tuner au mieux la résolution.

LIEN (https://github.com/nathmo/FlexProbeOptimisation/blob/main/report.md) vers script python (utilisable en version numérique)

En outre, en ce qui concerne le cahier des charges, notre projet est conforme à l’exception du point A.4 (Voir page 24). En effet, nous n’utilisons pas de vis à pas fin, mais des vis à pas normal. Le principe de vis différentielle avec des vis à pas normal nous permet d’augmenter considérablement notre résolution et justifie donc le non-respect du cahier des charges, de plus ce système permet également d’apporter une idée originale au projet.

4.1: Schéma de la table à 3 lames

### 4.2 Discuter les effets des tolérances de fabrication (typiquement ±3 µm pour l’usinage par électroérosion à fil) sur la performance du capteur

Nous avons toujours fait en sorte que toutes les épaisseurs soient supérieures à 100 μm, afin qu’une une tolérance de 3% sur l'épaisseur des lames ait peu d'influence sur la résolution du capteur, cependant celles-ci peuvent faire varier légèrement la rigidité et l’accumulation d’erreurs diminueraient les performances de notre capteur (notamment sur les lames utilisées pour la compensation de rigidité).

## 5 Construction

### 5.1 Argumenter les choix faits pour la construction

Nous avons décidé de concevoir un système dont le corps d'épreuve est composé de trois couches usinées par électroérosion en 2D pour que tout reste usinable par Wire EDM (Electrical Discharge Machining) Préalablement à cela, il est nécessaire de faire quelques opérations d’usinage 3 axes conventionnelles pour le système de fixation des plaques entre elles.

Les couches sont vissées ensemble et séparées par des morceaux de clinquants afin de limiter au maximum les frottements lors des mouvements des différentes couches. Nous utilisons parfois des lames dont le ratio longueur-largeur est supérieur à 60, il nous était donc nécessaire d’inclure des supports afin d’éviter des erreurs lors de l’usinage à cause des vibrations générées par le processus, les supports doivent être retirés à la fin de l’usinage. Le positionnement des divers supports a été spécialement étudié pour éviter des collisions lors de l’utilisation du capteur.

### 5.2 Argumenter les choix des matériaux

Nous avons choisi comme matériaux de l’alliage titane-6Al-4V. Ce matériau est très peu magnétique. Il est doté d'une résistance spécifique élevée et d'une excellente résistance à la corrosion. Il s'agit de l'un des alliages de titane les plus couramment utilisés, dans une large gamme d'applications où une faible densité et une excellente résistance à la corrosion sont nécessaires, notamment dans l'industrie aérospatiale et les applications biomécaniques (implants et prothèses).

Il possède également un module de Young de 110MPa.

## 6 Conclusion

En somme, notre projet DYNABAL est un capteur de force équilibré dynamiquement, possédant une fonction de compensation de rigidité. Notre solution respecte le cahier des charges et se distingue par son équilibrage SFMI*, son utilisation du principe de vis différentielle et son implémentation.

## 7 Annexes


Etape 1: Enlever les supports dus au processus d’électroérosion

Etape 2: Assembler les 3 couches du capteur

### 7.1 Dessin de construction de l’ensemble du capteur de force

Pour assembler l’ensemble du mécanisme, on commence tout d’abord par l’assemblage du capteur de force.


Etape 2: Montage de l'actionneur

Etape 3: Assembler les dernières parties du capteur dont la sonde

Une fois l’assemblage du capteur de force terminé, il ne reste plus qu’à monter l’intégralité du mécanisme comme ci-dessous :

Etape 1: Montage du support


Etape 3: Montage de l’actionneur 2

Etape 4: Assemblage du second actionneur

Etape 5: Montage des actionneurs sur le mécanisme


Etape 6: Montage du moteur sur le mécanisme

Etape 7: Visser vis M3 sur le mécanisme

Etape 8: Le mécanisme est assemblé

1 2 | 3 4 5 6 7 8
| 12,5

Tolérances Générales : ISO 2768-mk; AngleScrewBlocActuator

Mod. | | Mod. | | | Dessiné | 12.05.2023 | Groupe 36 | Echelle 4:1

Contrôlé

Conf aux norm

Bon pour exéc.

Sans nomenclature séparée | | | | N° de commande
Nomenclature sép de même N° | | Matiere | Acier Inox | Origine | | Format A4 | Nb feuilles 1 | Feuille N° 1
Nomenclature sép de N° diff | | Masse | 0,004 kg | Remplace

Dénomination | | | | N° de dessin

1 | 2 | 3 | 4
A


Tolérances Générales : ISO 2768-mk

Mod. | | Mod. | | | Dessiné | 12.05.2023 | Groupe 36 | Echelle 2:1

Contrôlé

Conf aux norm

Bon pour exéc.

Sans nomenclature séparée | | | | N° de commande
Nomenclature sép de même N° | | Matiere | Acier Inox | Origine | | Format A4 | Nb feuilles 1 | Feuille N° 1
Nomenclature sép de N° diff | | Masse | 0,011 kg | Remplace

Dénomination AxisLinear | | | | N° de dessin

1 | 2 | 3 | 4 | 5 | 6 | 7 | 8
A

Vue Isométrique :

Tolérances Générales : ISO 2768-mk

Mod. | | Mod. | | | Dessiné | 12.05.2023 | Groupe 36 | Echelle 2:1

Contrôlé

Conf aux norm

Bon pour exéc.

Sans nomenclature séparée | | | | N° de commande
Nomenclature sép de même N° | | Matiere | Acier Inox | Origine | | Format A3 | Nb feuilles 1 | Feuille N° 1
Nomenclature sép de N° diff | | Masse | 0,04 kg | Remplace

MotorDifferentialMountingBra Dénomination cket | | | | N° de dessin

1 | 2 | 3 | 4 | 5 | 6 | 7 | 8
A

Vue Isométrique :

Tolérances Générales : ISO 2768-mk

Mod. | | Mod. | | | Dessiné | 12.05.2023 | Groupe 36 | Echelle 4:1

Contrôlé

Conf aux norm

Bon pour exéc.

Sans nomenclature séparée | | | | N° de commande
Nomenclature sép de même N° | | Matiere | Acier Inox | Origine | | Format A3 | Nb feuilles 1 | Feuille N° 1
Nomenclature sép de N° diff | | Masse | 0,011 kg | Remplace

Dénomination MotorMountDifferential | | | | N° de dessin

1 | 2 | 3 | 4 | 5 | 6 | 7 | 8
A

Vue Isométrique :

Tolérances Générales : ISO 2768-mk

Mod. | | Mod. | | | Dessiné | 12.05.2023 | Groupe 36 | Echelle 4:1

Contrôlé

Conf aux norm

Bon pour exéc.

Sans nomenclature séparée | | | | N° de commande
Nomenclature sép de même N° | | Matiere | POM | Origine | | Format A3 | Nb feuilles 1 | Feuille N° 1
Nomenclature sép de N° diff | | Masse | 0,001 kg | Remplace

Dénomination POMSliderAxis | | | | N° de dessin

1 | 2 | 3 | 4 | 5 | 6 | 7 | 8
A

Vue Isométrique :

Tolérances Générales : ISO 2768-mk

Mod. | | Mod. | | | Dessiné | 12.05.2023 | Groupe 36 | Echelle 4:1

Contrôlé

Conf aux norm

Bon pour exéc.

Sans nomenclature séparée | | | | N° de commande
Nomenclature sép de même N° | | Matiere | POM | Origine | | Format A3 | Nb feuilles 1 | Feuille N° 1
Nomenclature sép de N° diff | | Masse | 0,001 kg | Remplace

Dénomination POMSliderMotor | | | | N° de dessin

1 | 2 | 3 | 4 | 5 | 6 | 7 | 8
A

Vue Isométrique :

Tolérances Générales : ISO 2768-mk

Mod. | | Mod. | | | Dessiné | 12.05.2023 | Groupe 36 | Echelle 4:1

Contrôlé

Conf aux norm

Bon pour exéc.

Sans nomenclature séparée | | | | N° de commande
Nomenclature sép de même N° | | Matiere | POM | Origine | | Format A3 | Nb feuilles 1 | Feuille N° 1
Nomenclature sép de N° diff | | Masse | 0,001 kg | Remplace

Dénomination POMSliderMotorM25 | | | | N° de dessin

1 | 2 | 3 | 4
A


Tolérances Générales : ISO 2768-mk

Mod. | | Mod. | | | Dessiné | 10.05.2023 | Groupe 36 | Echelle 2:1

Contrôlé

Conf aux norm

Bon pour exéc.

Sans nomenclature séparée | | | | N° de commande
Nomenclature sép de même N° | | Matiere | Acier Inox | Origine | | Format A4 | Nb feuilles 1 | Feuille N° 1
Nomenclature sép de N° diff | | Masse | 0,002 kg | Remplace

Dénomination Screw | | | | N° de dessin

1 | 2 | 3 | 4 | 5 | 6 | 7 | 8
A

Vue Isométrique :

Tolérances Générales : ISO 2768-mk

Mod. | | Mod. | | | Dessiné | 12.05.2023 | Groupe 36 | Echelle 4:1

Contrôlé

Conf aux norm

Bon pour exéc.

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

Dénomination SliderFixtureM25 | | | | N° de dessin

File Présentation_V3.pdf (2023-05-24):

### Projet de Conception de mécanisme II : DYNABAL


Introduction

- Dynamomètre


Architecture Général


Équilibrage

- Mouvement opposé –> Inverseur de mouvement
- Moment annulé
- Masse optimisé


Principe de compensation de rigidité

Principe de réglage du zéro


système vis-écrou

- vis différentielle
- Anti-rotation et guidage
- Accouplement
- Rattrapage du jeu


Traduction en guidage Flexible


Concepts Originaux

Equilibrage SFMI à l’aide des roues; Principe de vis différentielle; Précontrainte d’usine; Système multicouches; Système de protection du mécanisme

Dimensionnement du mécanisme

- Minimisation du nombre de lammes
- Minimisation de la rigidité des lammes •Dimensionnent Réglage du zéro
- Calcul de la rigidité total à vide
•Dimensionnement pusher Réglage de la rigidité


Optimisation Python


Dimensionnent du pusher rigidité zéro


Validation du mécanisme

Contraintes maximales admissibles
SS = 1.5
✓Résistance du mécanisme

✓Marge d’optimisation

Débattement des articulations

Revue des performances


Assemblage vissé; Supports pour lames; Alliage Ti-6Al-4V; Construction


Conclusion

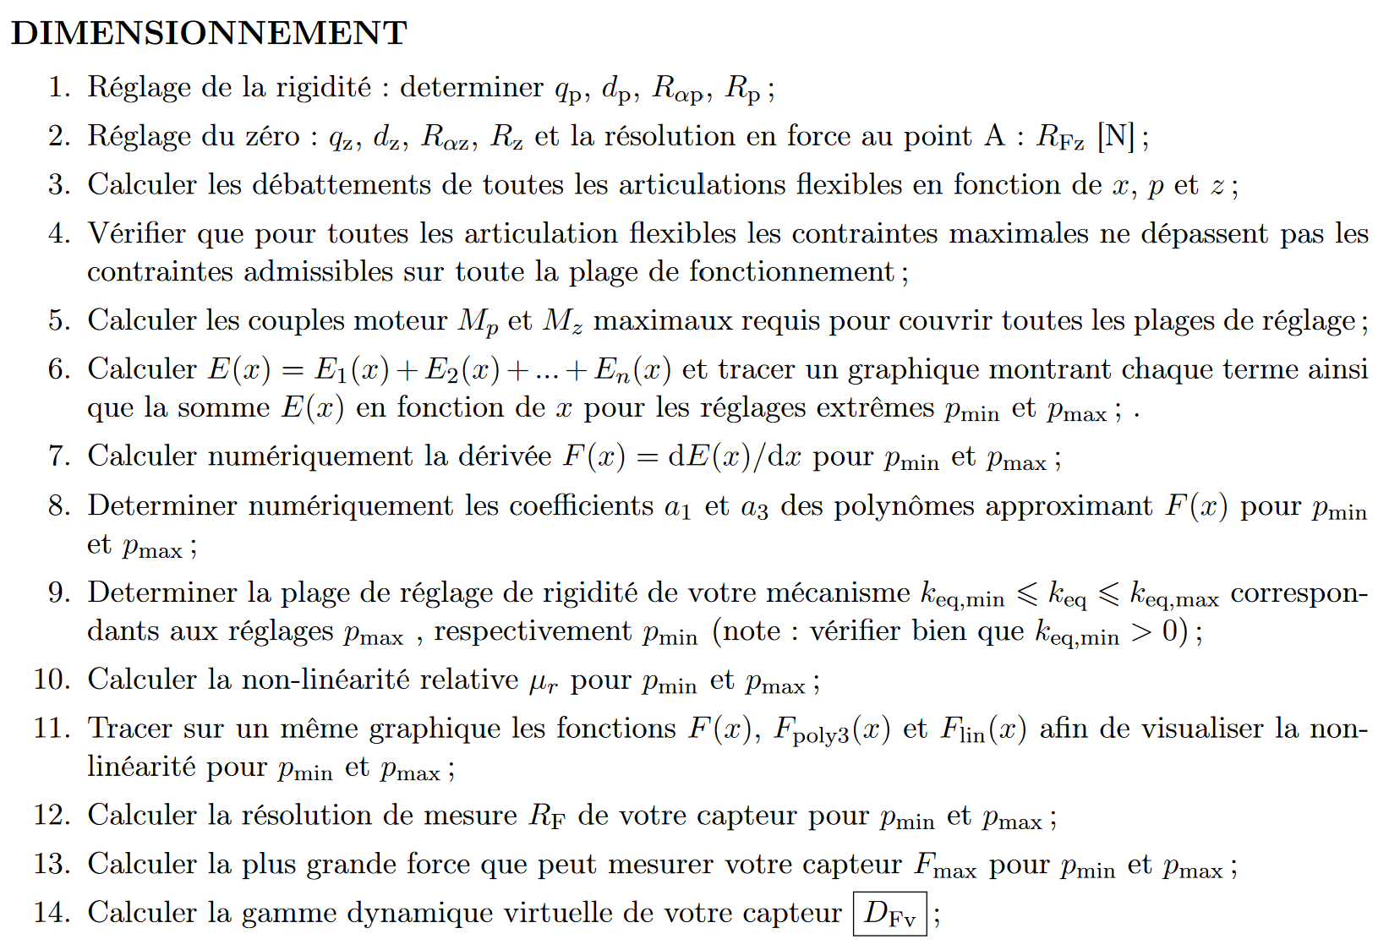
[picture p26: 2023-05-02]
img.png

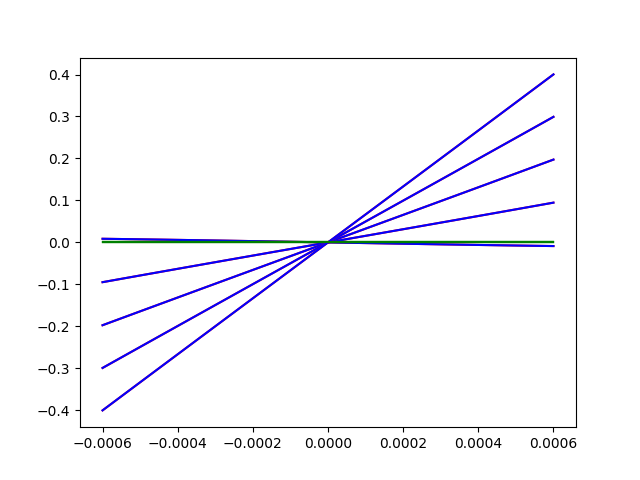
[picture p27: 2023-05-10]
ForceAsPositionANDPreloadNumTaylorLin.png

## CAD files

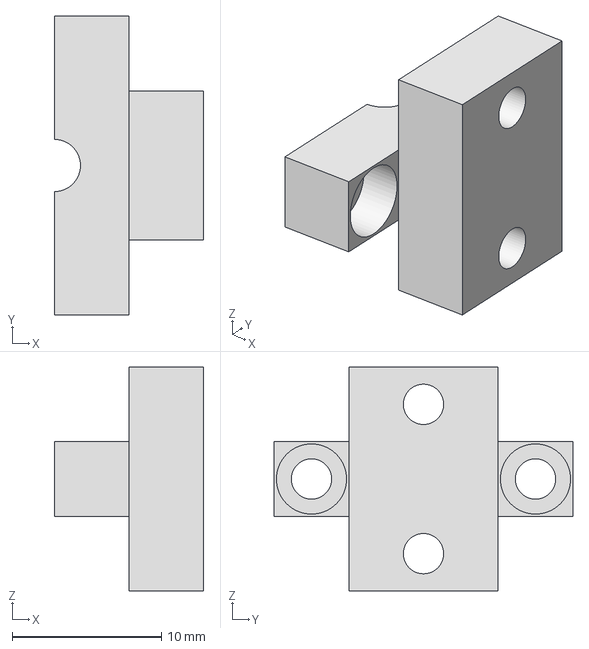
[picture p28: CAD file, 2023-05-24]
CAD3DIminaProbe/LinearAxis/SliderFixtureM25.stp
10.0 x 20.0 x 15.0 mm

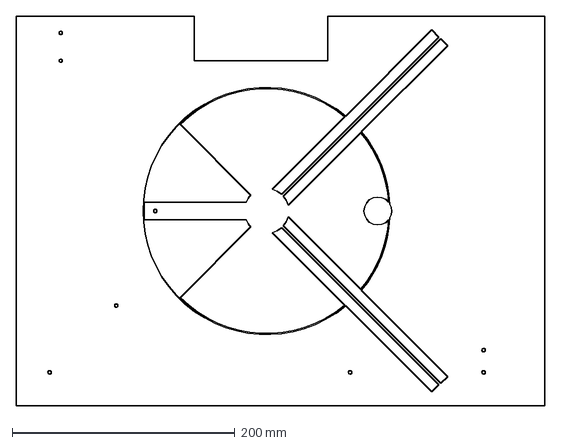
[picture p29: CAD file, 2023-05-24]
CAD3DIminaProbe/RoueMDF/WheelA.dxf
475.0 x 350.0 mm

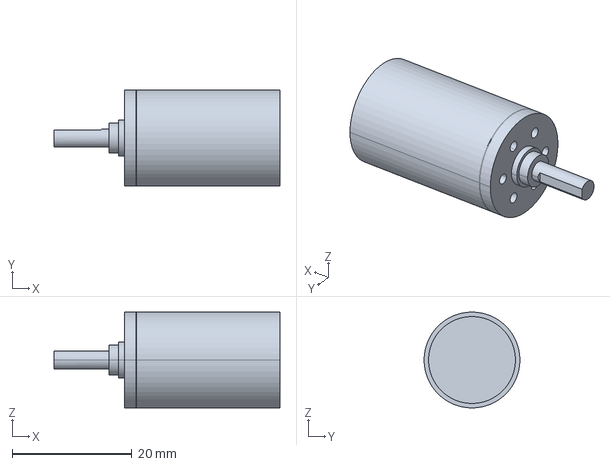
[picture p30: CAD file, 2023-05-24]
CAD3DIminaProbe/V2/GP16A_KL_4-Stufig-138342.stp
37.7 x 16.0 x 16.0 mm

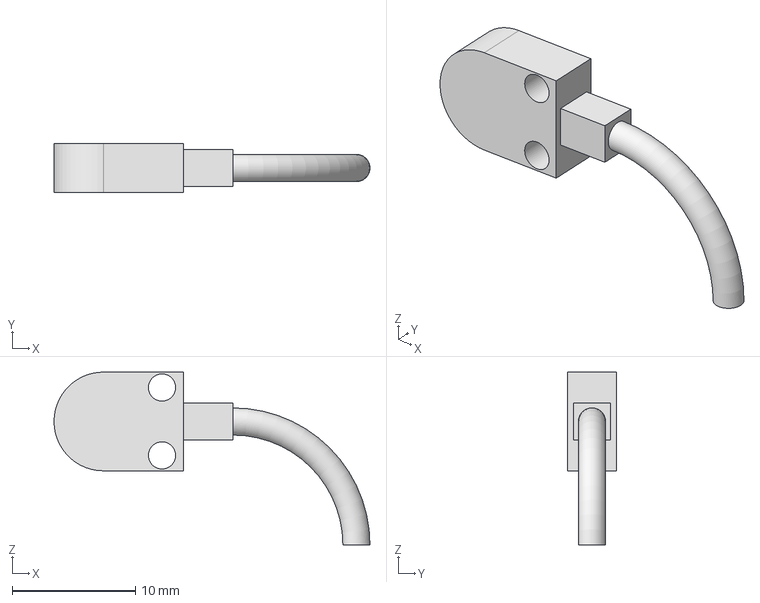
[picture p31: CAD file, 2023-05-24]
CAD3DIminaProbe/V4Roue/CapacitiveSensor.stp
25.6 x 4.00 x 14.0 mm

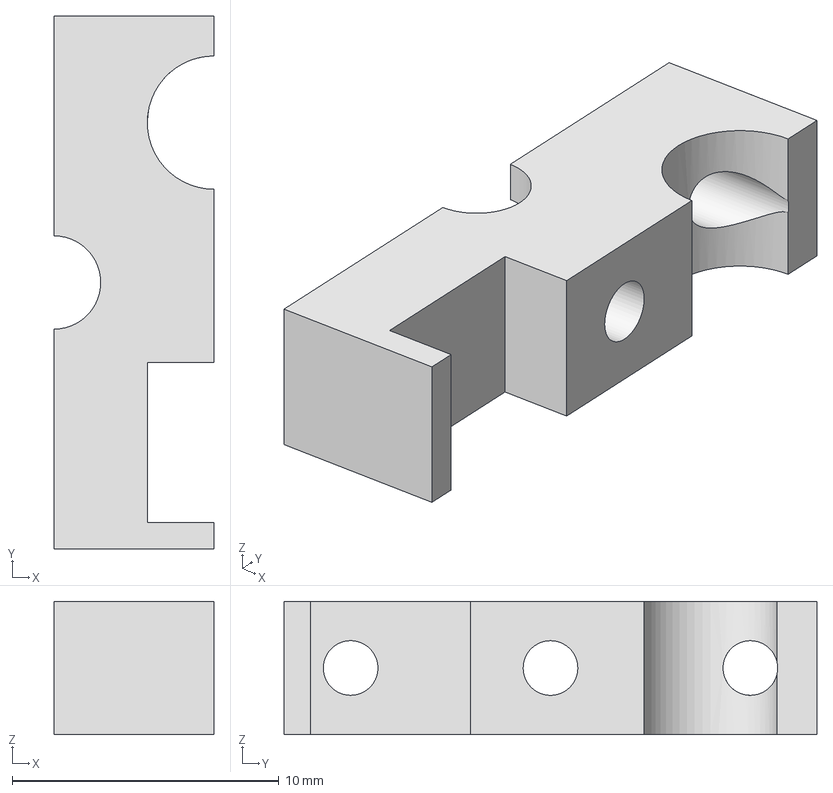
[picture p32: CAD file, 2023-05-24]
CAD3DIminaProbe/LinearAxis/POMSliderMotor.stp
6.00 x 20.0 x 5.00 mm

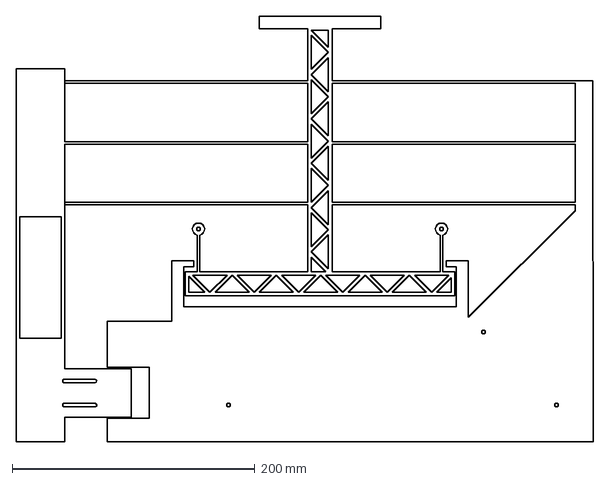
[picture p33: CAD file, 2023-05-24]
CAD3DIminaProbe/RoueMDF/WheelB.dxf
475.0 x 350.0 mm

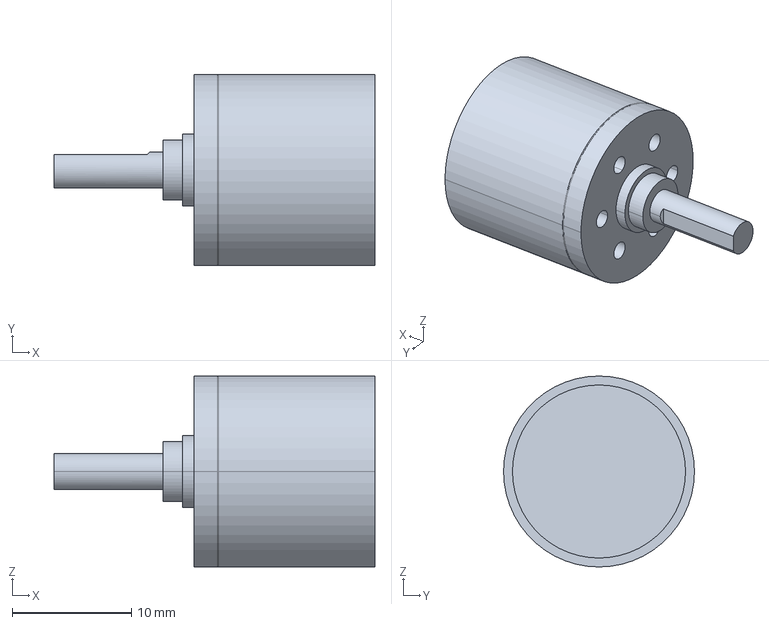
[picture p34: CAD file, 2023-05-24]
CAD3DIminaProbe/V2/GP16A_KL_1-Stufig-138333.stp
26.9 x 16.0 x 16.0 mm

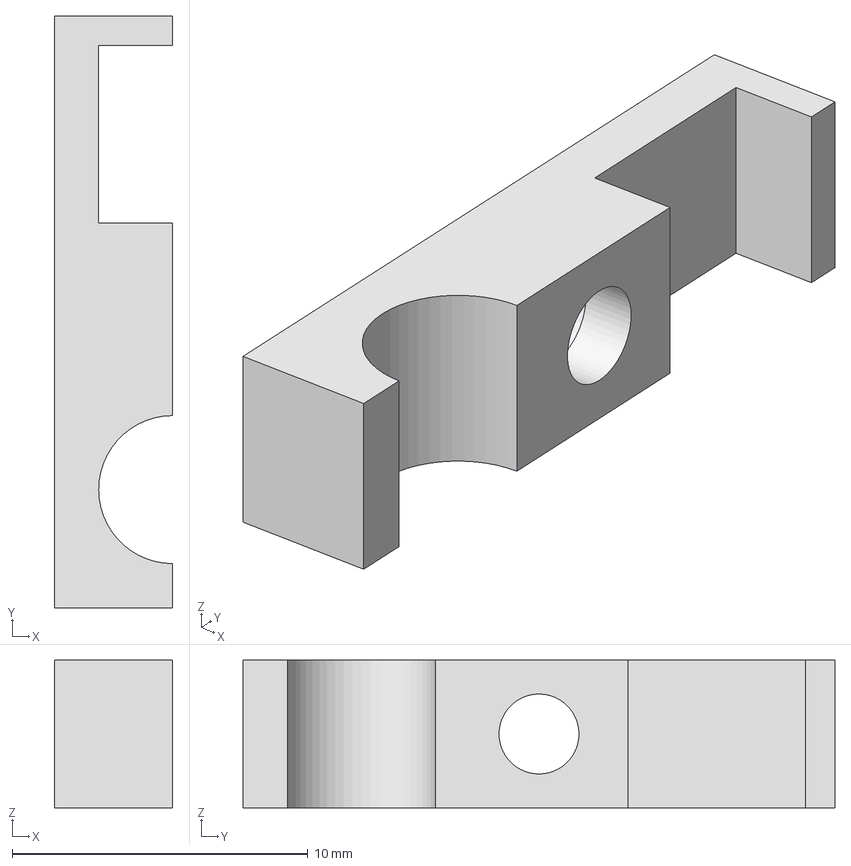
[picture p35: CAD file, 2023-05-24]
CAD3DIminaProbe/LinearAxis/POMSliderAxis.stp
4.00 x 20.0 x 5.00 mm

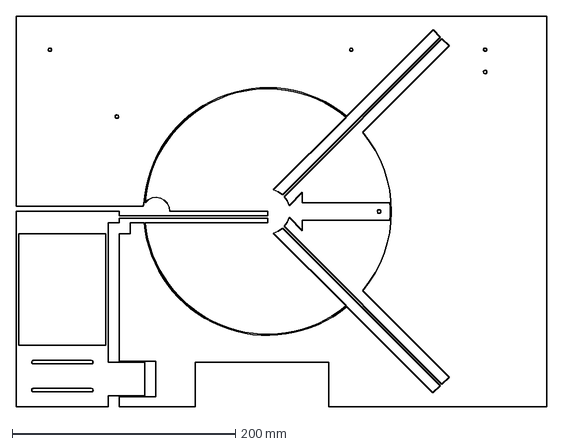
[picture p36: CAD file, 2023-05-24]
CAD3DIminaProbe/RoueMDF/WheelC.dxf
475.0 x 350.0 mm

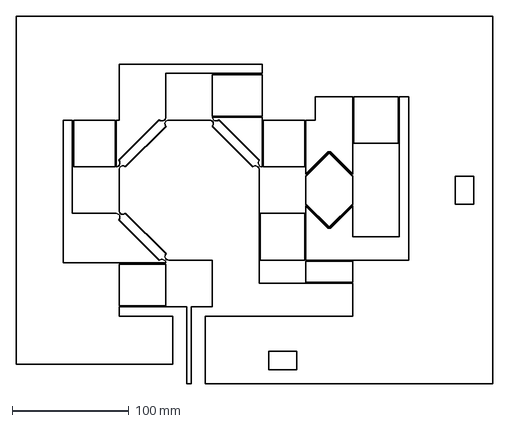
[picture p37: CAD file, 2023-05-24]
CAD3DIminaProbe/V2/TARS.dxf
408.0 x 314.8 mm

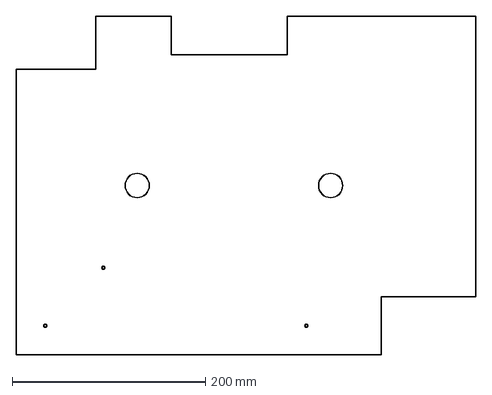
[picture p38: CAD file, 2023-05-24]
CAD3DIminaProbe/RoueMDF/WheelCover.dxf
475.0 x 350.0 mm

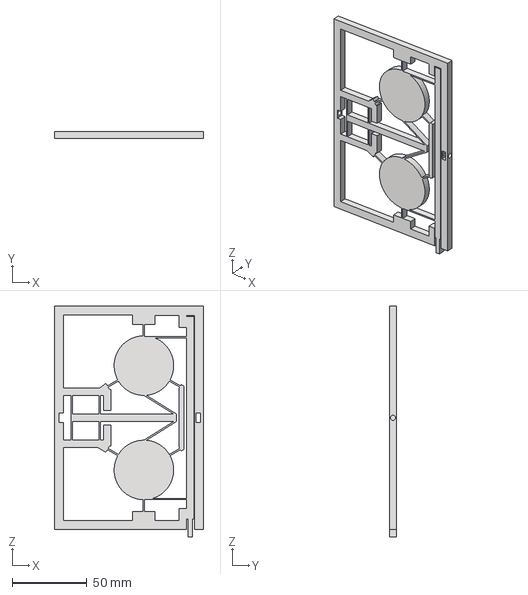
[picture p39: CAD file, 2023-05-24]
CAD3DIminaProbe/V2/FlexBlocK7.stp
100.0 x 5.00 x 155.0 mm

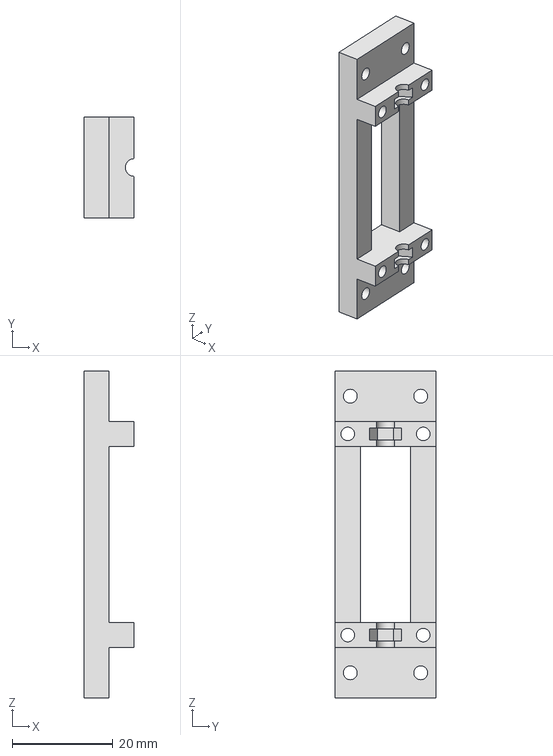
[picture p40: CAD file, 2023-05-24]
CAD3DIminaProbe/LinearAxis/MotorDifferentialMountingBracket.stp
10.0 x 20.0 x 65.0 mm

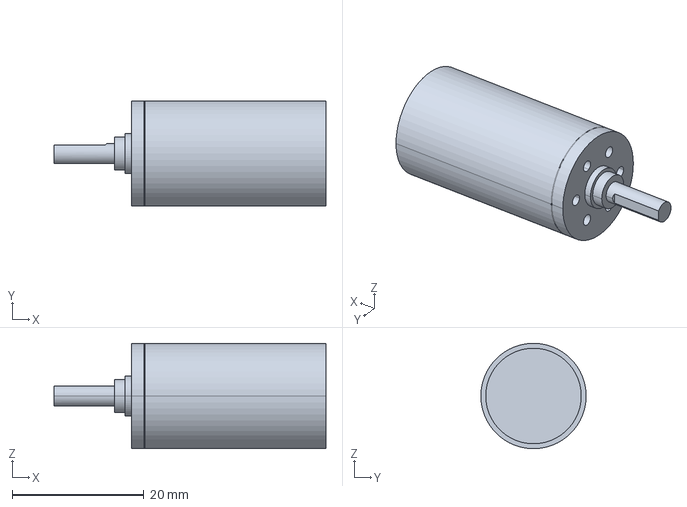
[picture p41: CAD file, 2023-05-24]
CAD3DIminaProbe/V2/GP16A_KL_5-Stufig-138347.stp
41.3 x 16.0 x 16.0 mm

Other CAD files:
CAD3DIminaProbe/LinearAxis/POMSliderMotorM25.stp
CAD3DIminaProbe/LinearAxis/AxisLinear.stp
CAD3DIminaProbe/V2/GP16A_2-Stufig-110322.stp
CAD3DIminaProbe/LinearAxis/MotorMountDifferential.stp
CAD3DIminaProbe/LinearAxis/AngleScrewBlocActuator.stp
CAD3DIminaProbe/LinearAxis/Screw.stp
CAD3DIminaProbe/RoueMDF/Assembly1.iam
CAD3DIminaProbe/RoueMDF/Cover.ipt
CAD3DIminaProbe/RoueMDF/Inverter.ipt
CAD3DIminaProbe/RoueMDF/OldVersions/Assembly1.0012.iam
CAD3DIminaProbe/RoueMDF/OldVersions/Inverter.0010.ipt
CAD3DIminaProbe/RoueMDF/OldVersions/Wheel1.0009.ipt
CAD3DIminaProbe/RoueMDF/OldVersions/Wheel2.0011.ipt
CAD3DIminaProbe/RoueMDF/Wheel1.ipt
CAD3DIminaProbe/RoueMDF/Wheel2.ipt
CAD3DIminaProbe/V1/283825_ec-max16_5w.ipt
CAD3DIminaProbe/V1/283825_ec-max16_5w.stp
CAD3DIminaProbe/V1/4145N198_Set Screw Precision Flexible Shaft Couplings.STEP
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

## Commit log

2023-04-25 wrote a skelleton class for a few type of blade spring
2023-04-30 improved workflow
    [Settings.xlsx]
2023-04-30 improved print aestetic
2023-05-01 added code to convert mouvment siez for each spring
    [Settings.xlsx]
2023-05-02 fully defined mechanism
    [Settings.xlsx]
2023-05-03 added way to edit text of md
    [Settings.xlsx]
2023-05-03 moved all parameter to the excel sheet, added code to compute table for zero andpusher k_eq
    [Settings.xlsx]
2023-05-04 added code to compute the dynamic range (still dirty
    [Settings.xlsx]
2023-05-05 all is computed right excpet non linéarity
    [Settings.xlsx]
2023-05-10 added polynial and relative linéarity
    [Settings.xlsx, SettingsMDF.xlsx]
2023-05-10 fixed linéar broken + derivation missing coeeficient
    [Settings.xlsx]
2023-05-10 removed useless folder
    [Settings.xlsx]
2023-05-19 small formattin issue
    [Settings.xlsx]
2023-05-24 pushed final report + CAD + presentation
    [283825_ec-max16_5w.ipt, 283825_ec-max16_5w.stp, 4145N198_Set Screw Precision Flexible Shaft Couplings.STEP, 4145N198_Set Screw Precision Flexible Shaft Couplin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]
